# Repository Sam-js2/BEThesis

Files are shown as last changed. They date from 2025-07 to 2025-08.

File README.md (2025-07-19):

# Supporting Material for Thesis C
**S Shelton z5359712**

This repository contains supporting material for Thesis C, including code, schematics and Altium design files.

A video of the device operating can be found [on YouTube here](https://youtu.be/sB7mTB_tMe0) [https://youtu.be/sB7mTB_tMe0].

The poster that was presented at SOFE2025 is here, as well as my Thesis C slides and an uncompressed copy of the thesis manuscript.

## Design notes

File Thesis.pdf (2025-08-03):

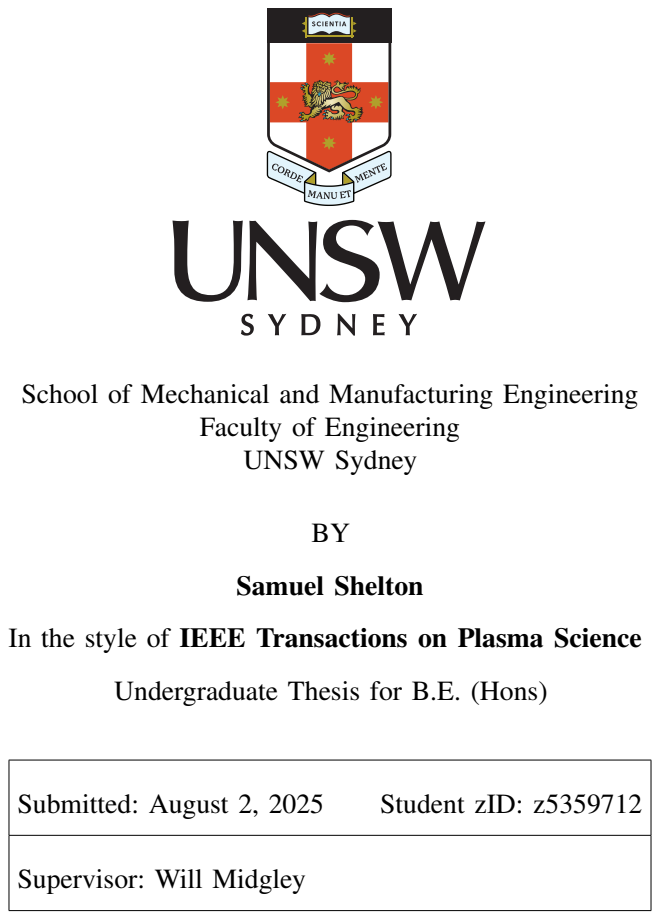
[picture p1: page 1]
BY Samuel Shelton; Submitted: August 2, 2025; Student zID: z5359712

School of Mechanical and Manufacturing Engineering

Faculty of Engineering
UNSW Sydney

In the style of IEEE Transactions on Plasma Science

Undergraduate Thesis for B.E. (Hons)

Supervisor: Will Midgley

MANUSCRIPT BACKGROUND

The work in this thesis was presented as a poster at the Symposium on Fusion Engineering, held 23–26 June 2025 on the MIT Campus in Cambridge, MA. This thesis is an extended version of a six-page conference paper that is being submitted to the IEEE Transactions on Plasma Science journal for the SOFE 2025 special issue. The formatting of this thesis is extremely close to the IEEE requirements (including the required biographies and Americanized spelling), but with some basic changes like the inclusion of an appendix (to house what would otherwise live on the journal’s website as supporting material) and the removal of references to submission and publication dates. Also please note that these pages are significantly denser than the 20 page (single column) limit, so the length of the paper is proportionally shorter.

ORIGINALITY STATEMENT

‘I hereby declare that this submission is my own work and to the best of my knowledge it contains no materials previously published or written by another person, or substantial proportions of material which have been accepted for the award of any other degree or diploma at UNSW or any other educational institution, except where due acknowledgement is made in the thesis. Any contribution made to the research by others, with whom I have worked at UNSW or elsewhere, is explicitly acknowledged in the thesis. I also declare that the intellectual content of this thesis is the product of my own work, except to the extent that assistance from others in the project’s design and conception or in style, presentation and linguistic expression is acknowledged.’

Signed:

Date:

# 2D Hall Arrays for High Resolution Tokamak Magnetic Field Imaging

Samuel Shelton and Will Midgley

Abstract—This paper presents the use of a two-dimensional array of magnetic field sensors designed to image the magnetic field produced in the vacuum vessel of the upcoming SOUTH tokamak. Designed to de-risk engineering efforts by allowing for precise mapping of toroidal and null field configurations within the plasma boundary region, this represents the first use of such a device within the context of fusion. Using low-noise circuitry and multiple analogue-to-digital converters in parallel, the device can achieve up to 20 kHz of analogue bandwidth across 256 sensors, with an effective sensitivity of 0.32 mT against a dynamic range exceeding ±150 mT. The device can also be operated in a real-time mode using a micro-controller, allowing interactive visualizations of magnetic fields for outreach and pedagogical purposes. Preliminary imagery and simulated reconstructions are presented, with the device intended to assist with the research and development, manufacturing and commissioning of the SOUTH tokamak in anticipation of a first pulse in late 2026.
Index Terms—tokamak, diagnostics, instrumentation, magnetovision, Hall effect, magnetic field mapping
I. INTRODUCTION
T HE SOUTH tokamak (shown in Fig. 1) is being developed at the University of New South Wales in Sydney, Australia as a student project called AtomCraft [1]. SOUTH—the Student Operated Undergraduate Tokamak with Hydrogen—will be the first tokamak designed and built entirely by undergraduates. It will be a compact, spherical tokamak employing conventional magnets and utilizing a combination of ohmic heating and electron cyclotron resonance heating (ECRH). The design is influenced primarily by the Danish NOTH tokamak [2] and its predecessor, Tokamak Energy’s ST-25 [3], with the coil and power supply designs inspired by the University of Seville’s SMART [4].
SOUTH is expected to operate with a toroidal on-axis magnetic field of 100 mT and an approximate 100 ms pulse, although these specifications are targets and are subject to change. The device has a major radius of approximately 0.3 m, with a vacuum vessel diameter of 30 cm. Initial plasma operations are expected to begin in late 2026, with plasma currents of 3 kA and plasma temperatures of about 10 eV expected [1]. AtomCraft’s primary focus is pedagogical, with the initiative focused on providing students with hands-on experience in fusion engineering from as early as their second undergraduate year. SOUTH is AtomCraft’s first project, with more nuclear-related projects and upgrades planned for the future.
S. Shelton and W. Midgley are with the School of Mechanical and Manufacturing Engineering, UNSW Sydney, and the SOUTH collaboration. Corresponding author W. Midgley, w.midgley@unsw.edu.au.
Supporting materials for this paper are available at https://github.com/Sam-js2/BEThesis (https://github.com/Sam-js2/BEThesis) and https://youtu.be/sB7mTB tMe0 (https://youtu.be/sB7mTB_tMe0)

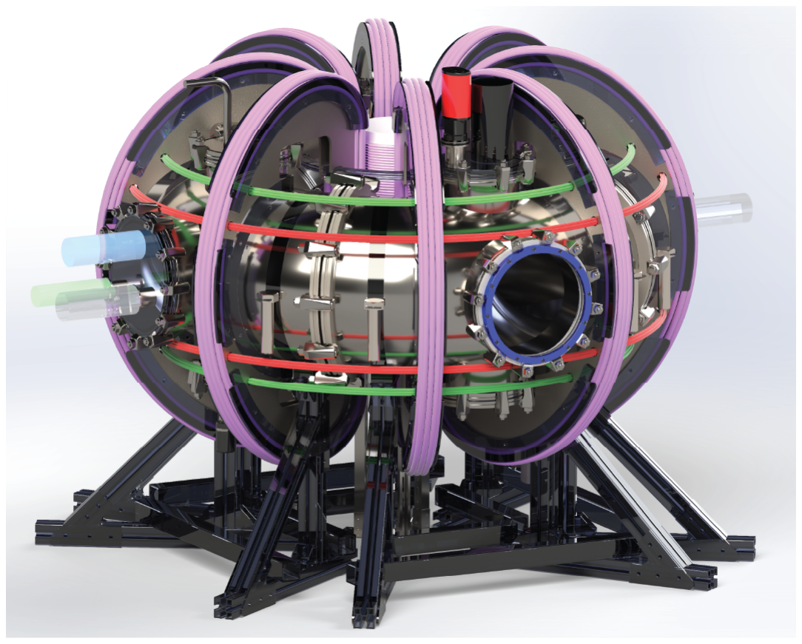
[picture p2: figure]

Fig. 1. A render of the upcoming SOUTH tokamak, with placeholder instrumentation, vacuum, fueling and RF equipment, with the ‘Princeton Dee‘ toroidal field (TF) coils are in purple and the poloidal field (PF) coils in red and green [1].

As a student project, AtomCraft operates under strict budgetary constraints and with a strong operational emphasis on safety and risk management. A significant portion of funding is sourced externally from philanthropic institutions and commercial fusion organizations, necessitating clear and communicable results for outreach purposes. The idea of a two-dimensional Hall array emerged as a tool to detect technical issues with the magnet system (particularly the critical toroidal field, produce by the ‘Princeton Dee’ magnets with a configuration as shown in Fig. 2) prior to plasma operation, with potential as an outreach and recruitment tool due to its visual and interactive nature.

A. Hall sensors and magnetic sensor arrays in Fusion
Hall effect sensors are widely used in fusion engineering for magnetic field monitoring [5], plasma diagnostics [6], and current sensing [7]. Low-density arrays have an established use in magnetic field mapping [8], and a high-density onedimensional array of Hall sensors has been demonstrated as an effective tool for measuring both vacuum and plasma-generated poloidal magnetic fields in magnetically confined steady-state plasmas [9].
1) ITER Magnetic Diagnostics: Chavan et al.’s 2009 paper in Fusion Engineering and Design serves as a summary of all the magnetic field diagnostics intended for use at ITER, while

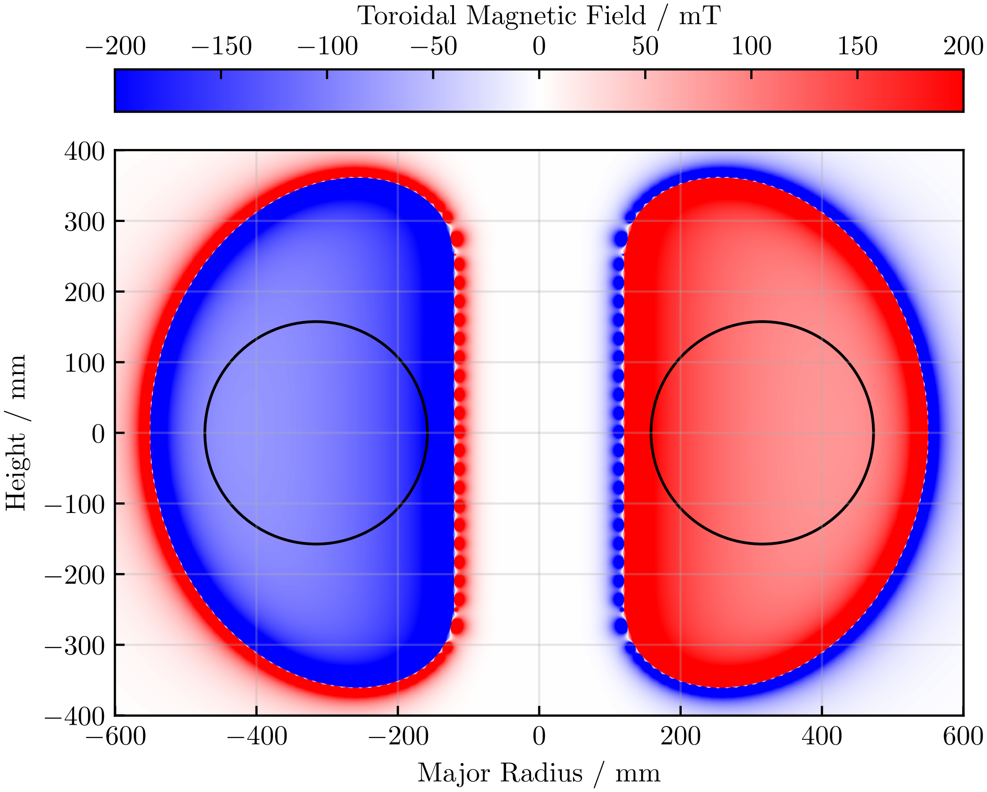
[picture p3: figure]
Major Radius / mm; Height / mm; Toroidal Magnetic Field / mT

Fig. 2. Toroidal magnetic field generated by SOUTH during a 3 kA plasma pulse. The field here is clipped to ±200 mT and was computed using the Biot-Savart law on a discretized model of the ‘Princeton Dee’ TF coils [1].

also discussing risks to the project [6]. The diagnostics set of ITER is to consist of 120 Hall probes for tangential field monitoring, 54 for radial field monitoring and 12 for toroidal field monitoring. This data is to be used to inform closed-loop control algorithms, and in post-pulse plasma reconstruction. These Hall probes are heavily redundant to account for any probe failures due to excess exposure to radiation [6]. Chavan et al. further identify the ITER-specific design drivers that informed the selection of this diagnostics setup. They include the ability to work over ITER’s long plasma pulse lengths, in the presence of high levels of neutron radiation, steep requirements for accuracy, precision and system availability, resistance to various kinds of electrical interference, and several requirements regarding data acquisition [6].
In a related follow-up paper, Duran ˇ et al. detail the design of a custom semiconductor Hall Effect sensor for use at ITER [11]. To address the challenges previously identified by Chavan et al. [6], Duran ˇ et al. use a metallic bismuth process and large sensor area to achieve sufficient radiation hardness. Their custom sensor, shown in Fig. 3a, is able to operate with sufficient sensitivities across a large range of magnetic field strengths up to ±6 T, with radiation hardness well in excess of anything commercially available. Fortunately, neutron irradiation and extended pulse lengths are not anticipated at SOUTH, and there is no closed loop control planned for the initial operating configuration. While ITER’s diagnostics are cutting edge, they are not as applicable to UNSW’s much smaller tokamak as might initially be expected.
2) Magnetic Field Diagnostics in Spherical Tokamaks: Other, spherical Tokamaks are more comparable to SOUTH geometrically. The QUEST Tokamak, a mid-sized spherical Tokamak located in Japan, uses an advanced closed-loop control system to achieve extremely stable plasma pulses lasting up to six hours [12]. A key part of this control system is a complex arrangement of Hall effect sensors (both single and tri-axial) located at key points on the outside of the vacuum vessel, as

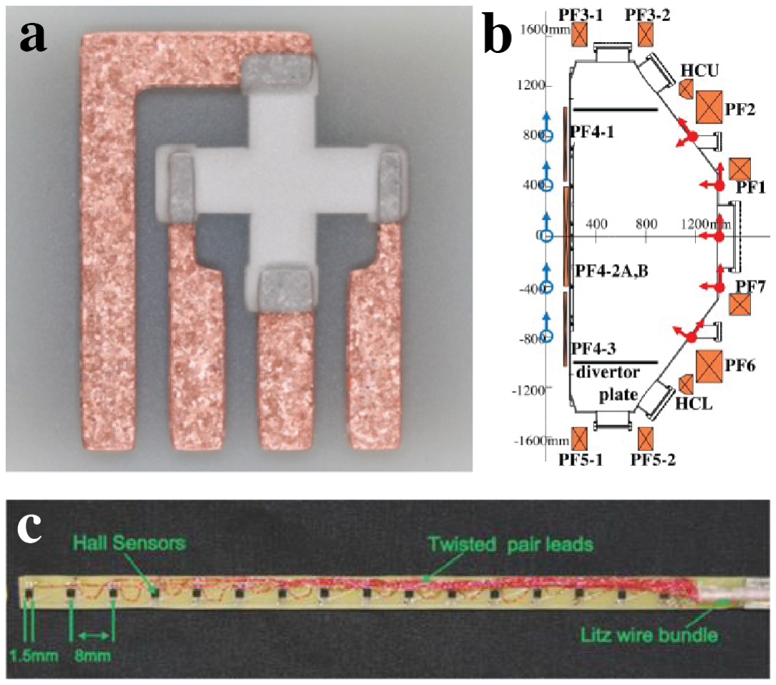
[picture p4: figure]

Fig. 3. Fusion applications of Hall sensors: a) Custom Lead-Bismuth Hall sensors for ITER [10]; b) Hall sensor placement for QUEST [5]; c) Insertable Hall array for poloidal field monitoring [9].

shown in Fig. 3b. These sensors provide output data which is integrated at 100 kHz, and fed into a control loop running at 4 kHz [5]. The sensors themselves are accurate over a range of ±1600 G (160 mT), which is comparable with the peak field expected on SOUTH. The Hall sensors here are particularly useful for combating the drift accumulated by the analog integration of Rogowski coil signals over long plasma pulses [5].
The small CASTOR tokamak featured a small array of eight commercial Hall effect sensor ICs integrated into the stainless steel vacuum vessel [10]. Duran ˇ et al.—the same Duran from ITER [11]—integrated sensors, power and signal ˇ conditioning circuitry onto a single small PCB, and put the entire device inside the Tokamak vacuum vessel—the first ‘invessel environment’ use of such sensors. The results prove the efficacy of commercial Hall effect sensors in environments with relatively low (compared to ITER) amounts of radiation and ambient temperatures up to 150 →C [10]. These results are very relevant to the SOUTH tokamak, which is expected to have conditions (in terms of radiation and ambient temperatures) similar to CASTOR. While Duran ˇ et al.’s work is not directly applicable to SOUTH because it is designed as a plasma diagnostic, the success of the project proves the viability of using commercial sensors for fusion applications.
3) Insertable Linear Array Probe: Stevenson et al.’s 2014 paper presents a linear array of 16 Hall effect sensors with a spacing of 8 mm, designed and fabricated on a printed circuit board [9]. This linear array (essentially a long, thin stick, as shown in Fig. 3c) is then inserted into the plasma through a hole in the vacuum vessel, and rotated around its axis of insertion to capture a full range of data. This implementation is extremely innovative and the most comparable existing design to what is proposed in this paper, and the use of twisted pairs, differential amplifiers and analogue anti-aliasing filters distinguish it as

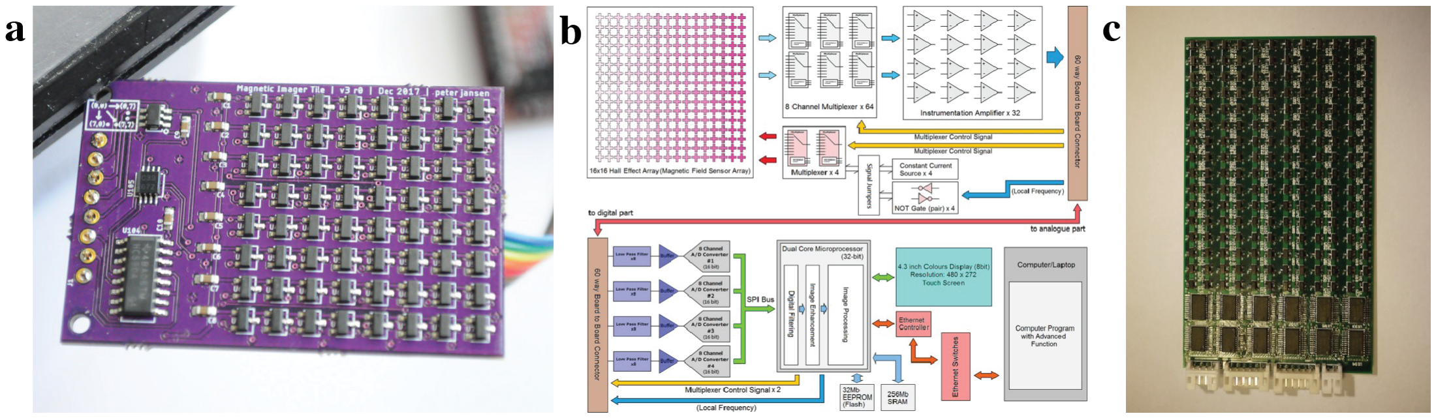
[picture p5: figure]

Fig. 4. Non-fusion applications of Hall arrays: a) Jansen’s Tile V3 [13]; b) Block diagram of Liang’s implementation [17]; c) Gaussense PCB [14].

the most complete implementation thus far.

B. Hall Arrays Outside of Fusion
Two-dimensional Hall arrays have been used outside of fusion as educational tools [13], in consumer electronics [14], and for non-destructive testing [17] and metallic object detection [18]. These devices all share a basic systems architecture underpinned by the use of multiplexed sensors, but implementations vary widely in terms of the data acquisition architecture and varying levels of analog filtering and complexity.
1) The Works of Peter Jansen: Peter Jansen’s work on these sensors on Hackaday served as a strong initial inspiration for this project. Jansen’s first Hall board was a 12 → 12 array that featured closely packed Hall Effect ICs fed into an analog-todigital converter (ADC) through cascaded I2C multiplexers. This implementation was slow—only achieving 10–30 samples per second (SPS) operation depending on the microcontroller used—mostly due to the speed of the I2C bus [15]. His next iteration, version 3.0 (shown in Fig. 4a), used a smaller 8 → 8 array and a binary counter connected to a clock to operate the multiplexers, enabling higher sampling rates up to 2,000 SPS [13].
While a great improvement, Janesen notes that the implementation is still bottlenecked by the slow ADC [13], and future devices could get around this by using a more powerful microcontroller. All of Jansen’s tiles suffer from a notable lack of any form of buffering or filtering, leaving the digitized signal to be susceptible to aliasing and rendering the entire setup vulnerable to electromagnetic interference. The PCB is also designed without a ground plane, among other issues that make the design susceptible to both the creation and absorption of EMI, necessitating a complete analog overhaul if the device were ever to be applied to fusion.
2) Real-time Magnetovision Camera: Liang et al.’s 2017 paper details a well designed and tightly integrated magnetovision imaging device [17]. Their device features a 16→16 array of custom Hall effect sensors whose outputs are multiplexed, buffered and sampled with an ADC—four in parallel for the 16 → 16 array—commanded by a microcontroller, which also coordinates the operation of the custom Hall effect sensors, as shown in Fig. 3b. Liang et al. apply best practice analog design using anit-aliasing filters and buffers, and completely separate the digital and analog PCBs to provide a level of modularity that makes manufacturing and testing easier, while also allowing for the digital components to be readily swapped out.
Liang et al. ran their SPI busses at 21 MHz and stored the excessive amount of data generated in discrete external memory, before sending it to a PC for analysis over ethernet [17]. Although designed to operate in ‘real-time,’ Liang et al. still achieve an impressive 600 SPS, more than enough for their specific use case but not enough for imaging the fast changing fields on SOUTH. This real-time application is also why a bilinear approach is used over the preferable but much more computationally intensive bicubic method for spatial interpolation. The design itself is also much to bulky to fit inside SOUTH’s vacuum vessel, but the innovative use of separate modular analog and digital PCBs could provide a path to compact and performant implementation.
3) Hall Arrays for User Interface Design: Liang et al.¹ proposed the use of an array of commercial Hall effect sensors as a way to sense the orientation of a writing stylus for a digital tablet display in their 2012 paper [14]. This Guassense technology was designed to enable devices to distinguish between stylus and finger inputs, sense the tilt and angle of a stylus, and detect a stylus hovering over the surface of a screen. Guassense was designed to augment existing devices, being placed behind LCD screens to add a new layer of user interactivity.
The hardware implementation, shown in Fig. 4c, contained 192 commercial Hall sensors multiplexed into a microcontroller’s inbuilt ADC. Bicubic interpolation was used to enhance the spatial resolution of images, and the polling rate was “consistently above 60 fps” [14]. Guassense suffers from most the same issues as Jansen’s implementations, and could benefit greatly from the incorporation of a proper buffering and filtering regime. It is worth commending the vision of Guassense: since its publication in 2012, Apple has gone on to successfully commercialize many of the unique goals of the project, namely the detection of stylus angle, tilt and hover [16]. While Apple doesn’t use an array of Hall effect sensors, Liang et al. successfully anticipated a market demand that

1A different Liang et al.. from [17].

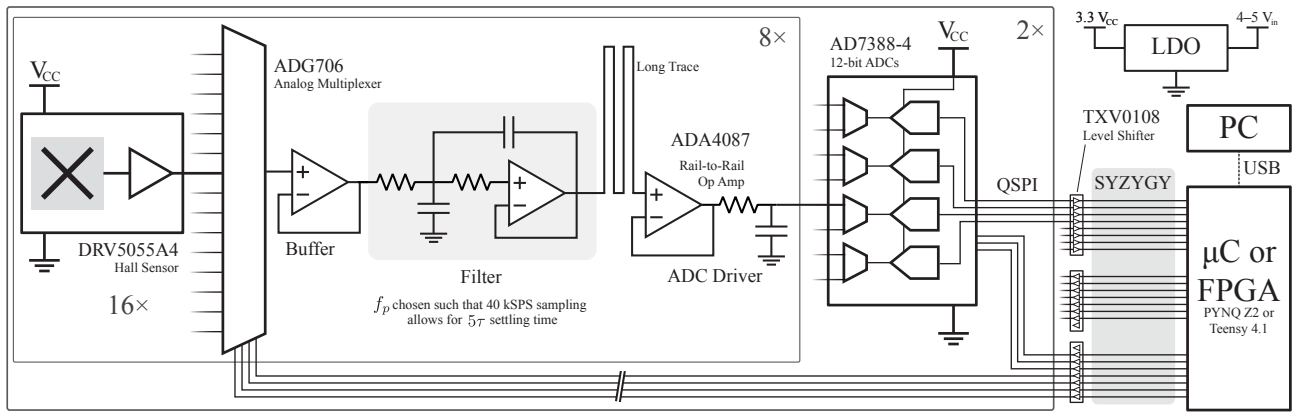
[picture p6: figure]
μC or FPGA; PYNQ Z2 or Teensy 4.1; DRV5055A4 Hall Sensor; VCC; ADG706 Analog Multiplexer; ADA4087; Buffer; Filter; ADC Driver; AD7388-4 12-bit ADCs; QSPI; SYZYGY; TXV0108 Level Shifter; chosen such that 40 kSPS sampling; allows for; settling time; LDO; Rail-to-Rail; USB; Op Amp; Long Trace; 3.3 VCC; 4–5 Vin

Fig. 5. Simplified circuit schematic showing the operation of the device.

would be only be realized more than a decade later.
4) Unpackaged Scanned Array: Cai et al.’s 2024 paper presents an array of 256 unpackaged (not contained in black plastic packages) Hall effect sensors that moved around on an X–Y drive to image a large area at an extremely high resolution [18]. Cai et al. are primarily concerned with spatial fidelity, so the use of unpackaged sensors allow the ‘pixels’ to be placed extremely close together, and the X–Y drive allows them to combine adjacent images to enhance both resolution and frame size. Cai et al. use external data acquisition boards, power supplies and control systems, so while the sensor itself is compact, the system still has a large overall footprint. While Cai et al.’s work is likely the least applicable to fusion applications of the devices discussed due to its extremely slow sampling rate, the use of unpackaged sensors has potential for future, more advanced devices.
C. Tokamak-specific Requirements for Hall Sensors
Based on existing implementations of Hall arrays both inside and outside of fusion and identified design constraints, the following were identified as the key properties required of a Hall array for use in magnetic field imaging on the SOUTH tokamak:
Sensitivity and Range: The array must measure both the strong toroidal field at approximately 100 mT and potential near-zero stray radial magnetic field components; an effective sensitivity of ↑ 1 mT is highly desirable.
Bandwidth and Sampling: Given the short pulse duration of 100 ms, the array requires a high analog bandwidth and associated sampling rate. A bandwidth exceeding 10 kHz— the PWM switching speed of SOUTH’s power supplies—is desirable.
Miniaturization: The array must fit within the vacuum vessels and through its standard flanges with a maximum width of 150 mm, while still covering the plasma boundary region of interest.
Environmental: The array must maintain a low noise floor (in order to achieve the desired sensitivity) and resist environmental sources of electromagnetic interference (EMI), including switching transients and RF interference, particularly around the industrial, scientific and medical (ISM) band at 13.56 MHz.
Existing magnetic field diagnostics in Tokamaks exist largely in service of physics applications, rather than in verifying the engineering itself and the ability to construct the magnetic field conditions intended. This is largely due to the much higher degree of engineering confidence in large scale projects like ITER, especially when compared to undergraduate work at UNSW. What diagnostics do exist are largely external to the vacuum vessel itself and are predominantly coil based, sacrificing almost all spatial resolution for temporal resolution and bandwidth.

II. METHODOLOGY &DEVICE DESCRIPTION
The final device works by simultaneously sampling eight sensors using two discrete ADCs, with 16:1 multiplexing into each filter and additional 2:1 multiplexing in-package on the ADC ICs; the device operating methodology summarised in Fig.
5. The analog and digital electronics are physically separated, allowing the analog sensor board to fit inside the vacuum vessel while the digital control board is located externally. This modular design also supports multiple digital processing configurations, customized for specific use cases. A 1/16th scale prototype was constructed to de-risk the final design, which was manufactured and assembled by a PCB assemblyhouse in China that used a combination of standard and specialized imported components.
A. Analog Electronics
The selected Hall sensor is the Texas Instruments DRV5055A4, which supports a measurement range up to ±179 mT when powered at 3.3 V and offers an analog bandwidth of 20 kHz [19]. Each sensor outputs a voltage proportional to the magnetic field (V ↓ B), with zero field corresponding to VCC/2. This architecture enables all 256 sensors to share a common reference with both ADCs, ensures that all voltages remain within the linear region of all operational op-amps, and provides some common-mode immunity from EMI.

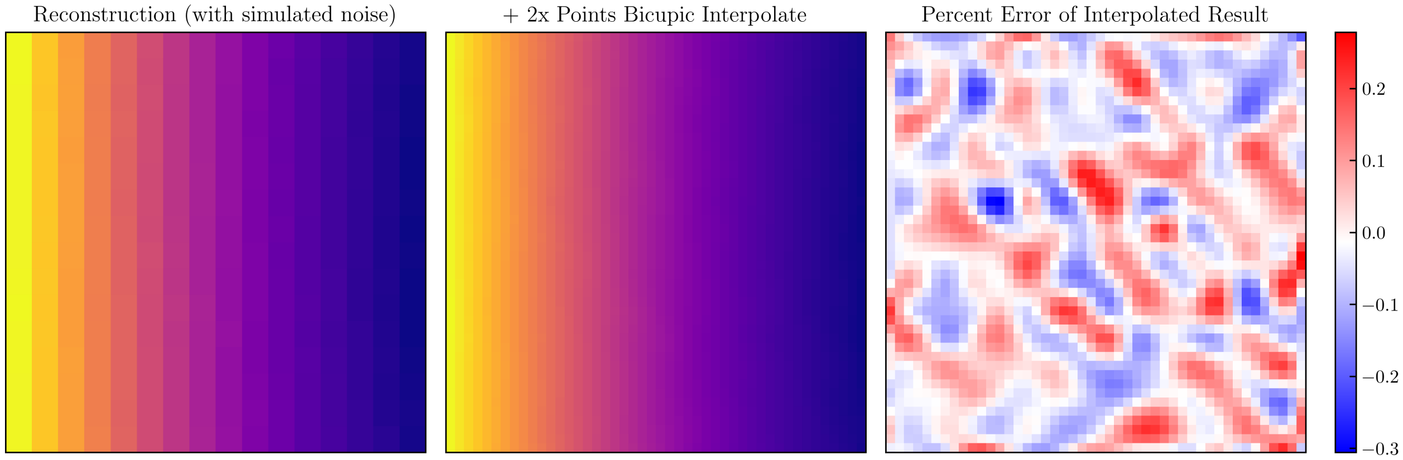
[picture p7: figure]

Fig. 6. Effects of bicubic interpolation, and error of interpolated result of reconstructed images, sharing a reconstruction model with Fig. 9.

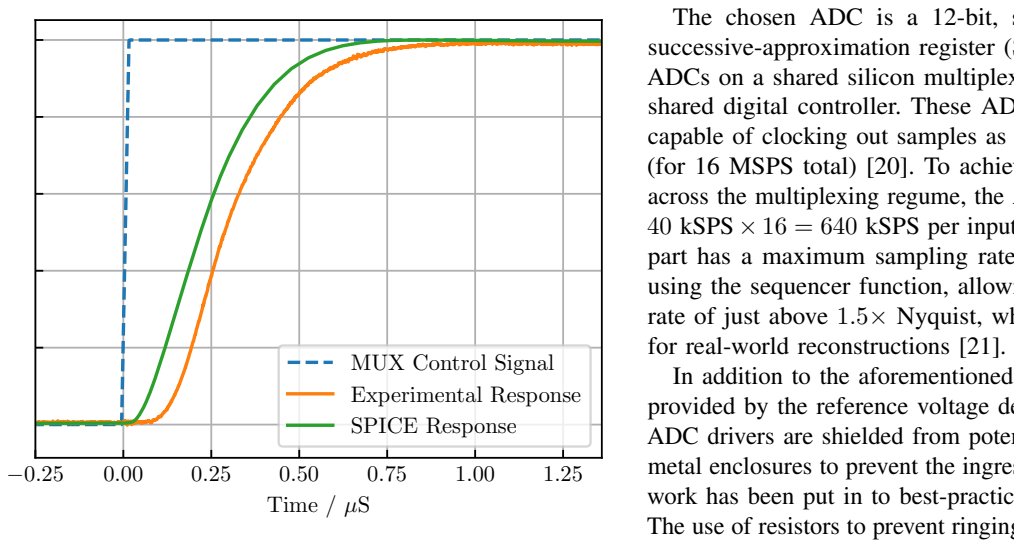
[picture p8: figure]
Time / µS; MUX Control Signal Experimental Response SPICE Response; for real-world reconstructions [21].

Fig. 7. Normalized experimental and simulated (with LTspice) filter settling behavior. The LTspice model is also shown in Fig. 11, and the experimental data was captured simultaneously with that of Fig. 15.

Sensor outputs are routed through high-performance analog multiplexers, buffered by low-noise rail-to-rail op-amps, and fed through single-stage Sallen-Key low-pass filters, before being buffered again by an ADC driver and digitized. The filter schematic is shown in Fig. 11, with an LTspice simulation of the filter response compared with the experimental settling shown in Fig. 7. The filter’s pole frequency, fp ↔ 1.2 MHz, is tuned to allow five time constants of settling at a sampling rate of 40 kSPS, after accounting for the increased sampling rate required for multiplexing. This filter mitigates high-frequency switching noise and RF interference but does not serve as an anti-aliasing filter. Consequently, the system is susceptible to aliasing from interference in the 20–1,000 kHz range, but most sources of external noise (including the ISM band) should be sufficiently suppressed. The inability to implement effective anti-aliasing without incurring significant cost is the primary limitation of the multiplexed topology.

The chosen ADC is a 12-bit, simultaneously sampling, successive-approximation register (SAR) part, featuring four ADCs on a shared silicon multiplexed to eight inputs with a shared digital controller. These ADCs share a quad-SPI bus capable of clocking out samples as fast as 4 MSPS per ADC (for 16 MSPS total) [20]. To achieve the Nyquist frequency across the multiplexing regume, the ADC must sample at least 40 kSPS → 16 = 640 kSPS per input channel, and the selected part has a maximum sampling rate of 1 MSPS per channel using the sequencer function, allowing a maximum sampling rate of just above 1.5→ Nyquist, which should be acceptable

In addition to the aforementioned common-mode immunity provided by the reference voltage design, both the ADCs and ADC drivers are shielded from potential interference inside µmetal enclosures to prevent the ingress of noise, and significant work has been put in to best-practice PCB design approaches. The use of resistors to prevent ringing, multiple stitched ground planes, digital and analog traces intersecting across layers at 90→ and a liberal deployment of LC filters in the power supply circuitry all contribute to reducing the generation and ingress of EMI.

B. Digital Electronics
The compact dimensions inside SOUTH’s vacuum vessel necessitate a separate digital control assembly. The main analog PCB includes three buffer/level shifter ICs which enable operation with both 3.3 V and 1.6 V logic, allowing interfacing with a wide range of controllers over a standard, high-performance SYZYGY FPGA connector. So far two compatible digital interfaces have been designed: one for userfriendly, interactive operation using a microcontroller, and another for high-performance data acquisition using an FPGA. The microcontroller-based solution uses a Teensy 4.1 [22] and is designed for sampling at up to 6 kSPS using dual hardware SPI interfaces. The Teensy can support 24 MHz onewire SPI, but can achieve 48 MHz with reduced stability. In this configuration, the ADC’s built-in hardware oversampling can be used to reduce bandwidth and mitigate aliasing, while also decreasing the amount of data produced. Full-rate sampling is not feasible due to bus speed and memory limitations.
To ensure data can be communicated correctly between the microcontroller and PC analysis software, a proprietary datapacket has been developed, with a layout as shown in Tab. I. This packet includes many synchronous bits at the start and end of the binary data, to make separating packets easier with inbluilt python and MATLAB functions like serial.readuntil. The packet includes empty space (the packet size padded to 512 bytes) and a version number to allow future expansion, and includes a packet counter and space reserved for CRC checksums to prevent both packet loss and data corruption. An example of the microcontroller digital logic operation is shown in Fig. 15 in the results section, and a representative sample of the microcontroller code is contained in Lst. 1 in the Appendix.

TABLE I
STRUCTURE OF SERIAL PACKETS
Field Name | Type | Bytes Description
sync1 | uint8_t | 1 | Sync byte 1 (0xAA)
sync2 | uint8_t | 1 | Sync byte 2 (0xBB)
sync3 | uint8_t | 1 | Sync byte 3 (0xCC)
sync4 | uint8_t | 1 | Sync byte 4 (0xDD)
count | uint32_t | 4 | Packet counter
timeStamp | uint32_t | 4 | Optional timestamp
dataSize | uint16_t | 2 | Number of uint16_ts
version | uint8_t | 1 | Packet version (0x01)
flags | uint8_t | 1 | Reserved/unused flags
data | uint16_t[192] | 384 | Data payload
spareData | uint8_t[104] | 104 | Reserved
CRC | uint32_t | 4 | Space for Checksum
sync5 | uint8_t | 1 | Sync byte 5 (0xEE)
sync6 | uint8_t | 1 | Sync byte 6 (0xFF)
sync7 | uint8_t | 1 | Sync byte 7 (0x11)
sync8 | uint8_t | 1 | Sync byte 8 (0x22)
Total | | 512 | Total packet size in bytes

The FPGA implementation uses a Pynq Z2 FPGA development board, capable of exceeding the 40 kSPS Nyquist frequency required for the 20 kHz sensor bandwidth. This is achieved using two four-wire SPI interfaces in parallel at bus speeds exceeding 50 MHz. The FPGA configuration is intended for high-performance, triggered measurements, though real-time interaction has been demonstrated as possible by other groups [17] and could be developed in the future.

C. Power Supply
Due to the analog electronics’ reliance on the power rail for both a supply and reference voltages, a low-noise linear dropout regulator (LDO) is used to provide a stable and clean 3.3 V common carrier voltage from an input voltage in the range of 4–5 V. PSice simulations of this power supply, shown in Fig. 8, show acceptable startup behavior that meets the requirements set by the ADC [20], [23]. MOLEX micro-fit cables were chosen because of their extremely small PCB footprint, robust supply chain and adjacency with the mini-fit JR line of products already in use by SOUTH, with crimping tools already available in various accessible research labs. Ideally the device should

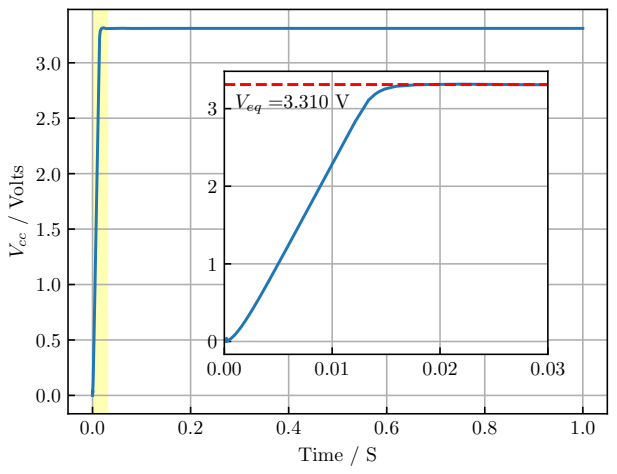
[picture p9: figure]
Time / S; Vcc / Volts; Veq =3.310

Fig. 8. PScipe simulation of power supply output voltage, with detail showing startup time. In steady-state operation noise is expected to be 4.4 µVRMS [23].

receive its 4–5 V input voltage from an external linear power supply, but low-noise operation (as low as 4.4 µVRMS [23]) is still achievable when powered from a quality switching mode converter. The LDO is connected to several ground planes to ensure adequate cooling, but running on closer to 4 Vin is advisable to prevent excessive heat dissipation.

D. Data Processing & Analysis
To convert the raw ADC output codes into meaningful images, each code is mapped to a spatial location in two dimensions, then converted to a voltage and a magnetic field using the sensor sensitivity and DC offset. This processing is performed externally on a host computer. For the FPGAbased implementation, additional processing is required to apply a phase correction to each sensor’s fully reconstructed (with sin x/x interpolation) analog waveforms to correct for rolling-shutter effects that are an inevitable consequence of the multiplexed topology. For real-time operations, the acquisition rate is significantly faster than the display refresh rate, rendering rolling shutter effects negligible.
Bicubic interpolation between adjacent sensors has been employed in previous Hall array implementations [14], [17], and is used here in post-processing where the computational cost is negligible. Fig. 14 presents selected results enhanced via bicubic interpolation; this method is effective when the spatial resolution of the sensor array exceeds the granularity of the magnetic field being reconstructed, such as in the case of the tokamak’s toroidal field cross-section, but localized field—such as those generated by small button magnets—are vulnerable to artifacting.
E. Intended Use in SOUTH Tokamak
The primary application of the device in the SOUTH tokamak is to validate the magnitude and spatial configuration of the toroidal field, which should ideally look like the field shown in Fig. 2. Fig. 9 illustrates a numerically simulated

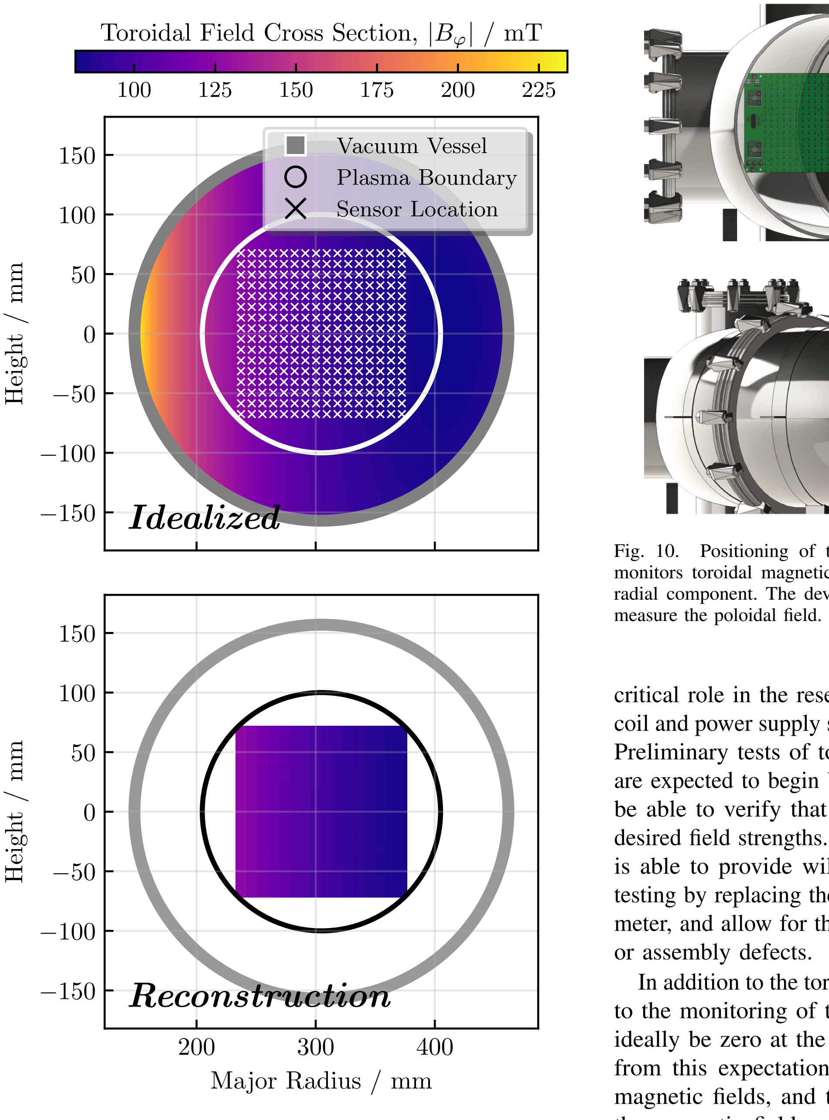
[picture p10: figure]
Toroidal Field Cross Section, |B'| / mT; Height / mm; Idealized; Vacuum Vessel Plasma Boundary Sensor Location; Major Radius / mm; Reconstruction; measure the poloidal field.; or assembly defects.

Fig. 9. Idealized plot shows sensor geometry (a 9 mm pitch) within SOUTH and an ideal field simulation during the ‘flat top‘ of a 3 kA pulse, shared with Fig. 2; the reconstructed field accounts for sensor geometry and noise.

toroidal field for a 3 kA plasma in SOUTH, alongside a simulated reconstruction incorporating modeled device noise. The imaging capability of the array is expected to confirm the characteristic Bω ↗ 1/R relationship and allow comparison with multiphysics simulations. The device could also potentially offer some quantitative measurement of magnetic field ripple; a device bandwidth of 20 kHz will be able to get some basic measurements of the ripple in the 10 kHz switching frequency device, but because that 10 kHz signal is a square wave a full reconstruction would not be possible (and would require a sampling rate of at least 30–50 kSPS by rule of thumb [21]). While applying this device to the full assembled tokamak system (in the configuration shown in the upper segment of Fig. 10) is the primary design goal, the device will also serve a

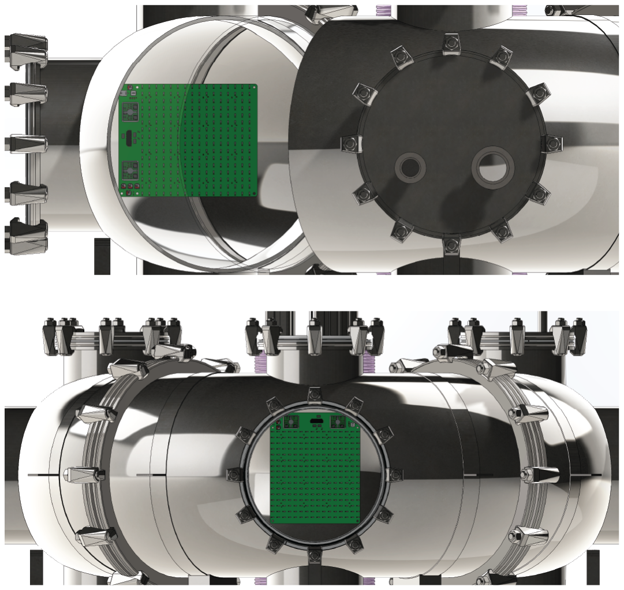
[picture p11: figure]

Fig. 10. Positioning of the tile within SOUTH. The top configuration monitors toroidal magnetic field while the bottom configuration monitors radial component. The device could also be positioned facing upwards to

critical role in the research and development of the individual coil and power supply systems before the full design integration. Preliminary tests of toroidal field coils at fractional currents are expected to begin by the end of 2025, and this device will be able to verify that the applied currents are achieving the desired field strengths. The instant feedback that the Hall array is able to provide will be able to improve the efficiency of testing by replacing the use of a single, lower-bandwidth gauss meter, and allow for the timely detection of any manufacturing

In addition to the toroidal field, the device can also be applied to the monitoring of the radial magnetic field, which should ideally be zero at the center of the toroidal field. Deviations from this expectation would indicate the presence of stray magnetic fields, and this would in turn indicate issues with the magnetic field system that could be flagged for further investigation. Since each sensor measures the field component parallel to its normal vector, the array must be positioned to intersect the field lines of interest, as shown in the bottom section of Fig. 10. A poloidal application, similar to [9], is also possible, but this would be particularly intolerant of sensor misalignment and require a high sensitivity.

F. Initial 1/16 Scale Prototype
Because of the significant cost investment of the final device (each sensor cost about A$1 and each ADC about A$ 80, with a minimum order quantity of two devices) a 1/16th scale prototype was designed to test the PCB manufacturing quality and analog electronics. The prototype, shown in Fig. 11, featured a two-stage analog filter that was unstable in its manufactured state. After making some modifications to the filter and reducing it to a single stage, the filter achieved the performance shown in Fig. 11.

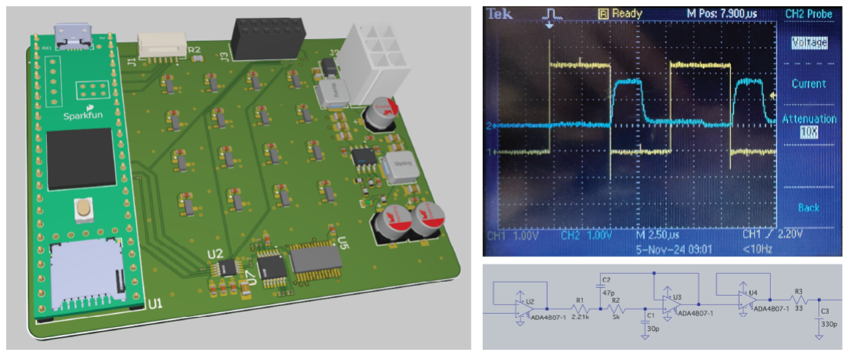
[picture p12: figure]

Fig. 11. 1/16th Scale Prototype, with experimental filter testing results and filter schematic shown.

The prototype used 0201 size components, initially chosen so that a full two-stage filter setup could be fit inside a surface-mount EMI shield, but the difficulty in modifying the components (because they were so small) combined with the dropping the second filtering stage informed a switch to much more accessible 0603 components for the final design. This decision was also influenced by the significant cost penalty that 0201 assembly incurred, and the increased parts availability (i.e., a wider range of resistances and capacitances to use a more favorable filter configuration) and flexibility provided by 0603 parts that could be soldered by hand to accommodate changes to the filters or drivers after initial manufacturing. Another key objective of the prototype was testing the manufacturing tolerances of the ‘via-in-pad’ technology, which dramatically reduces routing complexity by embedding vias directly into the very fine pitch (< 0.65 mm) pads of the multiplexers and op-amps. No short circuits between adjacent pads were identified by the manufacturer, and none were found during manual inspection. The prototype also functioned as a test-bed for the development of PC-based analysis software while the final device was still having its design finalized, parts sourced and circuit boards printed, dramatically accelerating the project’s software development timeline.

III. RESULTS
The final device (shown in Fig. 12) was delivered with no debilitating design of manufacturing defects, and testing to-date is indicative of a comprehensive fulfillment of the design goals outlined in the introduction. The micocontroller digital control board is capable of much faster sampling than anticipated, with sampling up to 10 kSPS possible. This makes further development of the FPGA implementation unnecessary until the full 40 kSPS sampling is required for full-bandwidth testing of SOUTH’s coils, anticipated for mid–late 2026. Interactive plotting in real-time also works reliably, although software Python and MATLAB-based serial frontends limit the data collection rate to about 250 SPS, meaning 10 kSPS sampling can only be achieved over short periods of time when taking a ‘triggered’ measurement. This means that an FPGA development board—with external, discrete and plentiful DRAM—is necessary for extended operation at high sampling rates.
Some preliminary static imagery (averaged over many acquisitions) is shown in Fig. 14, but the device’s functionality and dynamic imaging capabilities are best demonstrated more

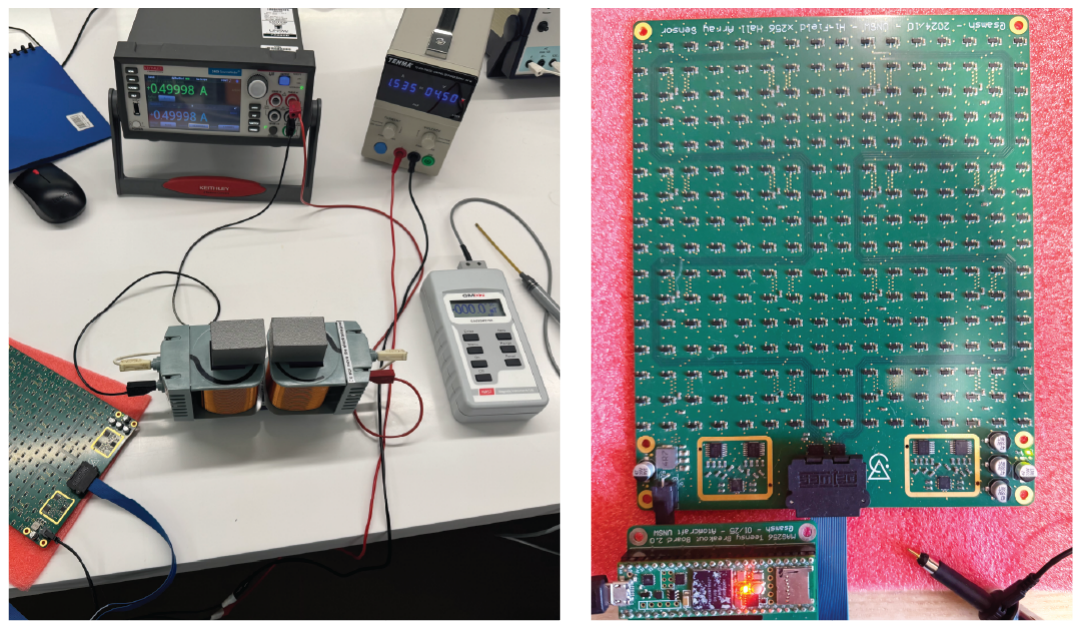
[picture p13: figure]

Fig. 12. Linearity calibration setup with source meter, gauss meter, and ferrite core electromagnet (left), and close-up of the completed device (right) with the Teensy digital controller board partially shown.

interactively as in the video contained within the supporting material or hosted on YouTube, here. This video should be considered essential viewing.

A. Quantification of Noise
The noise of all individual sensors were measured with no applied magnetic field over a sampling period of 10,000 samples, collected with a generous settling time to maximize the effectiveness of the analog electronics. As shown in Fig. 13, all 256 sensors perform similarly and there is no significant geometric correlation of noise statistics between adjacent sensors or sensors that share filters or ADCs. The device demonstrates a very low AC RMS noise floor below one leastsignificant bit or about 0.086 mT, with a corresponding effective sensitivity of 0.32 mT. The noise statistics do not drop off as expected with the introduction of hardware oversampling, likely because the noise floor is dominated by quantization noise. This indicates that future iterations could benefit from the use of higher-resolution ADCs, although the utility of such an improvement is questionable.
This is an exceptionally low noise floor, well in excess of the requirements identified as part of the projects literature review. This noise floor is low enough that it likely enables new uses of the device, specifically in the monitoring of SOUTH’s (much smaller) poloidal fields. The high dynamic range of the instrument, combined with its sensitivity, would allow for the monitoring of small amounts of ripple ontop of large DC magnetic fields.
B. Calibration
The DC offset at zero magnetic field was calculated using the same dataset as the noise measurements. Sensor calibration was performed with a ferrite-core electromagnet powered by a Tektronix/Keithley 2460 source-measure unit, generating a highly stable and uniform magnetic field. This field was measured with a four-digit gauss meter to be approximately 115 mT, with cross-sectional variations under 1%. Each sensor on the PCB recorded both positive and negative field measurements (i.e., aligned and anti-aligned to the same field). These high and low-field data points, along with the zero-field

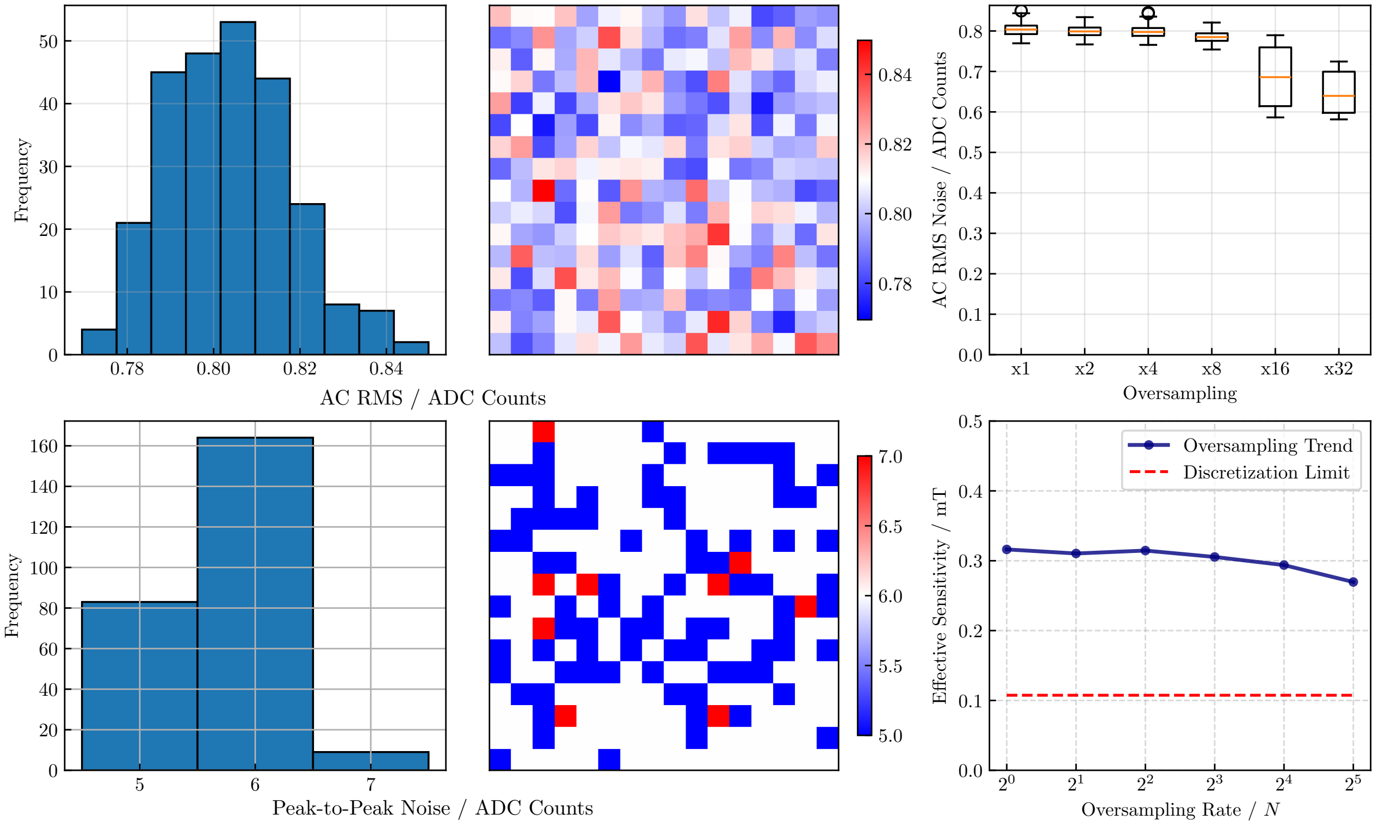
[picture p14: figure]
Frequency; Oversampling; AC RMS Noise / ADC Counts; Oversampling Rate / N; Eective Sensitivity / mT; Oversampling Trend Discretization Limit; Peak-to-Peak Noise / ADC Counts; AC RMS / ADC Counts

Fig. 13. Peak-to-peak and AC RMS noise data and spatial distributions, AC RMS noise boxplots as a function of hardware oversampling window size, and effective sensitivity as a function of hardware oversampling window size.

average, were binned into histograms and used to perform a
three-point linear regression, with the resulting sensitivities
shown in Fig. 14. This calibration focused on determining the linear sensitivity of each sensor, and not validating the sensor linearity that was already guaranteed by the manufacturer [19]. Both the linearity and DC offset constant show no significant or persistent geometric correlation across the sensor plane, which would be indicative of a misbehaving filter or some source of localized noise on the PCB, as shown in Fig. 14. While sensitive enough to meet the requirements set for the device, observed sensitivities were still generally below the quoted values from the sensors’ manufacturer [19], potentially indicating that the filters have a gain slightly but consistently higher than unity, which could be explained by capacitors generally erring on the side of being bellow the stated capacitance rather than above (although still within the quoted 5% tolerances).
C. Experimental Performance of Electronics
Using an oscilloscope with a logic analyzer add on, a full digital and analog capture of an acquisition event can be made simultaneously. Fig. 15 shows the full digital signal capture of the digital logic going to and from the micro-controller, running at a reduced sampling rate. This logic proves that everything is working as expected, and highlights where the parallelization provided by an FPGA could be used to dramatically increase performance. Timings could also be tightened to achieve higher a sampling rate by accounting for the time taken to move SPI results from the input buffer to memory, which would reduce the required programmed wait times between transactions. Similarly, Fig. 7 shows the experimental filter response of the final filter design, slightly improved over the prototype shown in Fig. 11. The filter settles slightly faster here with only a single Sallen-Key stage, at the cost of a more relaxed attenuation response in the frequency domain. The experimental filter is very close but still noticeably slower in settling than the LTspice simulation, which is likely due to either an overly optimistic spice model provided by the manufacture of the op-amp and/or multiplexer (either an overstated slew time or underquoted switching speed), or from the spice model not adequately modeling the effects of the ADC on the filter circuit (a lack of modeling of input capacitance, for example). Future iterations of the device should raise the pole frequency, fp, to combat this slower than expected performance.

IV. DISCUSSION
The scope of the 2D Hall array in this configuration is inherently limited to small, spherical tokamaks where the array dimensions can be reasonably compared to the toroidal region of interest while maintaining sufficient sensor granularity. This device offers small fusion endeavors a cost-effective alternative to the comprehensive field mapping solutions available to larger, more mature projects.
The device demonstrates significant pedagogical potential, serving as digital version of magnetic viewing film. It could

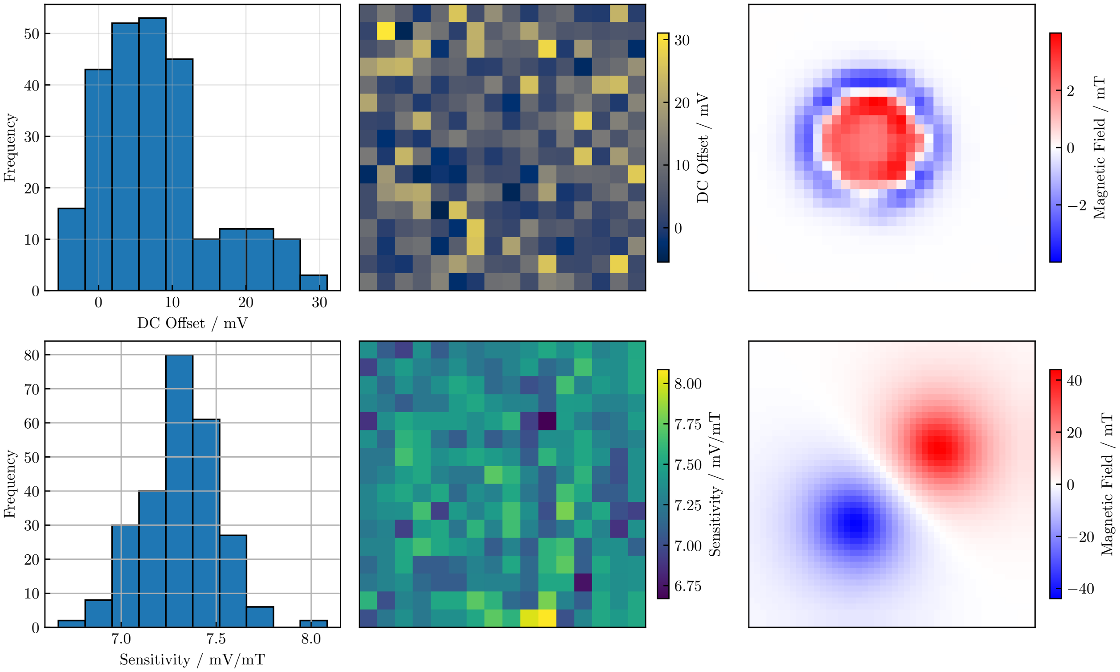
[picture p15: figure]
DC Oset / mV; Frequency; Sensitivity / mV/mT; Magnetic Field / mT

Fig. 14. Calibration results: DC offset with zero applied field (top); linear magnetic field sensitivity (bottom); preliminary imagery (right) of an Apple MagSafe charger and a very strong bar magnet, showing the use of bicubic interpolation. The manufacturer quotes an expected sensitivity of 7.5 mV/mT [19].

enhance undergraduate instruction in general physics and
introductory electromagnetism courses by enabling direct
observation of fundamental concepts, like the magnetic fields
produced by current-carrying wires. The visual and interactive nature of the device makes it particularly suitable for outreach activities, and AtomCraft will use it to attract new students recruits to the project and the University broadly, with the device expected to be presented to the general public at the upcoming UNSW Open Day in early September 2025.

The array’s sensitivity, dynamic range and low noise floor open possibilities for its use as a plasma diagnostic tool in SOUTH for monitoring poloidal fields (where the intrusion into the plasma is not as prohibitive to tokamak operations), as demonstrated previously [9]. However, its application in larger tokamaks like ITER or commercial reactors faces challenges. In addition to the aforementioned geometric limitations, its reliance on commercial sensors restricts operation in highradiation environments, a problem avoided by ITER’s custom bismuth sensors [6], for example. Additionally, the multiplexed topology introduces aliasing risks for high-frequency plasma instabilities above 20 kHz. Future iterations could explore custom sensors or more exotic analog filtering and ADC configurations to address these limitations, potentially expanding the device’s utility to both engineering validation and plasma physics in small-to-medium size fusion devices.

A. Immediate Future Developments
The immediate priority for future development of this work is the continued design of an FPGA digital control board which can ‘slot in’ to replace the Teensy microcontroller. A breakout board to adapt the connector that comes out of the device to interface with a Pynq Z2 FPGA development board has already been designed, manufactured and assembled, and some preliminary FPGA development has already commenced. The better than expected performance of the microcontroller implementation have lessened the requirement to have the FPGA ready as soon as possible, but it is still required to take full advantage of the bandwidth on offer and is therefore still a future goal.
B. Presentation at SOFE 2025
While presenting this work at the Symposium on Fusion Engineering 2025, on the MIT Campus in Cambridge, MA, there were a few attendees who had suggestions or observations about potential applications of the device, these are included here as potential future developments.
One attendee from the MIT Plasma Science and Fusion Center (PSFC) asked about the prospects of using a similar device submerged in liquid nitrogen for the monitoring of superconducting magnets, within the context of MIT PSFC’s new superconducting magnet test facility [24] which is being used for the development of new tokamaks and stellarators

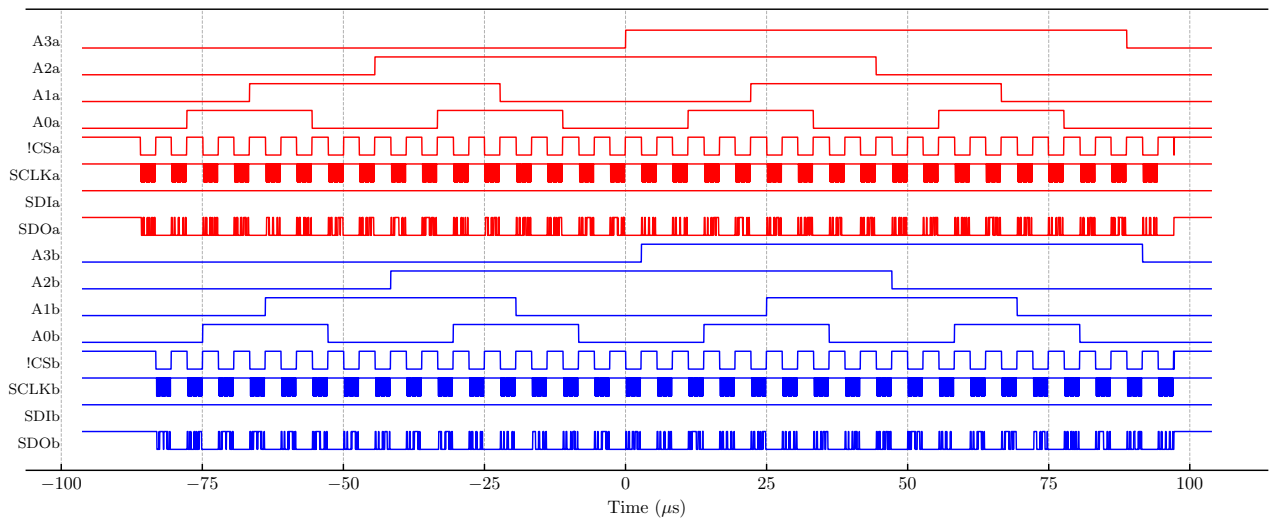
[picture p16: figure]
Time (µs); !CSa; SCLKa; SDIa; SDOa; !CSb; SCLKb; SDIb; SDOb

Fig. 15. Experimental capture of the digital logic behind a single ‘image’ taken using the digital channels of an oscilloscope (this data was recorded at the exact same time as that of Fig. 7). Compare this with the code shown in Listing 1 in the supporting material to get a better idea of what each SPI transaction is for. Note the very quick ‘reset sequencer’ pulse on the chip select lines towards the very end of the data.

like Commonwealth Fusion Systems’ (SP)ARC reactors [25]
and Type One Energy’s FPP [26].
This application is extremely novel and innovative, but
equally challenging and technically demanding. The device would need to be redesigned so that only the Hall sensors— and not any of the supporting electronics—get dipped into the liquid nitrogen, with all analog processing and data acquisition happening externally, and different, high-field Hall sensors would also need to be used. Getting the Hall sensors to function while submerged in liquid nitrogen initially seems like a technical hurdle, with the datasheet discouraging operation outside of a quite restrictive thermal envelope [19], but another attendee from OpenStar technologies (a New Zealandbased levitating dipole fusion company [27] that AtomCraft collaborates with) remarked that they semi-regularly use offthe-shelf Hall effect sensors in similar conditions with full functionality, even when operating well outside of datasheet specifications.
Another attendee from the Princeton Plasma Physics Laboratory (PPPL) asked about the possibility of using a similar array for liquid metal tomography and identified an extremely high dynamic range as critical for this application, with the ability to distinguish small fields (mT range) in the pretense of a very large background (multiple T) the key requirement. An array of Hall sensors is suited to this task, but likely custom sensors would be needed, potentially with a tuned analog bias current applied to cancel out the passive magnet field, as the dynamic range requirements are otherwise so extreme.
C. Future Collaboration with SMART Tokamak in Seville After networking and exchanging contact details at SOFE 2025, a preliminary collaboration between these authors and the SMART Tokamak team—a collaboration between the University of Seville and the PPPL [4]—has begun with the goal of using a small set of similar devices to monitor and control the alignment of coils during the re-assembly of the SMART tokamak, which is happening until late October 2025. The preliminary concept is to apply a ‘small’ DC currents to the tokamak’s magnetic coils, and then use a set of about six arrays in key locations to confirm that all the fields are adding as constructively as possible as each coil is moved into position and secured. The first author is expected to visit SMART in Seville in late 2025 to assist with this work, and communication is ongoing between the two teams currently.
V. CONCLUSION
This paper has presented the design, performance, and preliminary results of a high-resolution 2D Hall effect array device built to aid in the research and development of a small spherical tokamak. By functioning as a magnetic field camera, the arrays can image the toroidal fields within the region of plasma confinement and de-risk engineering efforts by verifying that generated magnetic fields match multiphysics simulations. The device demonstrates a high effective resolution of 0.32 mT, an average AC RMS noise floor of 0.086 mT and a dynamic range exceeding ±150 mT. The completed system provides a practical, cost-effective solution for magnetic field mapping in resource-constrained environments while offering substantial educational value. The low noise performance achieved with commercial components establishes a new benchmark for future developments of similar systems, in fusion engineering and beyond.
Following a positive reception from the fusion community at SOFE2025, this device will be used in the assembly of SOUTH in the medium-term future—up until late 2026—and will be applied shortly to the assembly and commissioning of the SMART tokamak, in preparation for its second experimental campaign envisioned to commence in late 2025/early 2026.

ACKNOWLEDGMENTS
We would like to thank all the students and academics of AtomCraft – especially Patrick Burr and Ed Obbard – for providing the context for this research, as well as enabling our access to facilities. Thank you to the lab staff in the mechatronics research laboratory and physics higher-years teaching laboratory for the use of their facilities, guidance and help with fabrication and testing.
Presentation of this work at SOFE2025 was funded by the Sir William Tyree foundation through the UNSW Nuclear Innovation Center Travel Award.

REFERENCES
[1] AtomCraft collaboration, private internal communications, 2024–2025.
[2] S. K. Nielsen et al., “First results from the NORTH tokamak,” Fusion Engineering and Design, vol. 166, p. 112288, May 2021, doi: 10.1016/j.fusengdes.2021.112288.
[3] A. Sykes et al., “The ST25 Tokamak for rapid technological development,” in 2013 IEEE 25th Symposium on Fusion Engineering (SOFE), Jun. 2013, pp. 1–4. doi: 10.1109/SOFE.2013.6635330.
[4] M. Agredano-Torres et al., “Coils and power supplies design for the SMART tokamak,” Fusion Engineering and Design, vol. 168, p. 112683, Jul. 2021, doi: 10.1016/j.fusengdes.2021.112683.
[5] M. Hasegawa et al., “Current status and prospect of plasma control system for steady-state operation on QUEST,” Fusion Engineering and Design, vol. 112, pp. 699–702, Nov. 2016, doi: 10.1016/j.fusengdes.2016.04.016.
[6] R. Chavan et al., “The magnetics diagnostic set for ITER,” Fusion Engineering and Design, vol. 84, no. 2, pp. 295–299, Jun. 2009, doi: 10.1016/j.fusengdes.2008.12.103.
[7] X. Wu, H. Huang, L. Peng, Y. Huang, and Y. Wang, “Algorithm Research on the Conductor Eccentricity of a Circular Dot Matrix Hall High Current Sensor for ITER,” IEEE Transactions on Plasma Science, vol. 50, no. 6, pp. 1962–1970, Jun. 2022, doi: 10.1109/TPS.2022.3173286.
[8] N. Marconato, E. Sartori, and G. Serianni, “Numerical and Experimental Assessment of the New Magnetic Field Configuration in SPIDER,” IEEE Transactions on Plasma Science, vol. 50, no. 11, pp. 3884–3889, Nov. 2022, doi: 10.1109/TPS.2022.3167859.
[9] B. A. Stevenson, S. F. Knowlton, G. J. Hartwell, J. D. Hanson, and D.
A. Maurer, “Hall probe measurements of the poloidal magnetic field in Compact Toroidal Hybrid plasmas,” Review of Scientific Instruments, vol. 85, no. 9, p. 093502, Sep. 2014, doi: 10.1063/1.4894209.
[10] I. Duran, O. Hronov ˇ | a, J. St ´ | ockel, J. Sentkerestiov ¨ | a, and J. Havlicek, ´
“Magnetic measurements using array of integrated Hall sensors on the CASTOR tokamak,” Review of Scientific Instruments, vol. 79, no. 10, p. 10F123, Oct. 2008, doi: 10.1063/1.2971209.
[11] I. Duran, S. Entler, M. Kohout, M. Ko ˇ | can, and G. Vayakis, “High ˇ
magnetic field test of bismuth Hall sensors for ITER steady state magnetic diagnostic,” Review of Scientific Instruments, vol. 87, no. 11, p. 11D446, Oct. 2016, doi: 10.1063/1.4964435.
[12] K. Hanada et al., “Overview of recent progress on steady state operation of all-metal plasma facing wall device QUEST,” Nuclear Materials and Energy, vol. 27, p. 101013, Jun. 2021, doi: 10.1016/j.nme.2021.101013.
[13] P. Jansen, “A Third, High-Speed Magnetic Imager Tile,” Hackerday.io, Feb. 12, 2018. [Online]. Available: https://hackaday.io/project/18518-iteration-8/log/91551-a-third-high-speed-magnetic-imager-tile. Accessed: Oct. 30, 2024.
[14] R. H. Liang, K. Y. Cheng, C. H. Su, C. T. Weng, B. Y. Chen, and D.
N. Yang, “Gausssense: attachable stylus sensing using magnetic sensor grid,” in Proceedings of the 25th annual ACM Symposium on User Interface Software and Technology, Cambridge, MA, Oct. 2012. doi: 10.1145/2380116.2380157.
[15] P. Jansen, “A Magnetic Imager Tile,” Hackerday.io, Aug. 29, 2017. [Online]. Available: https://hackaday.io/project/18518-iteration-8/log/64376-a-magnetic-imager-tile. Accessed: Oct. 30, 2024.
[16] “Apple introduces next-generation iPad Pro, supercharged by the M2 chip,” Apple Newsroom (Australia). Accessed: Nov. 06, 2024. [Online]. Available: https://www.apple.com/au/newsroom/2022/10/apple-introduces-next-generation-ipad-pro-supercharged-by-the-m2-chip/
[17] C.-W. Liang, E. Balaban, E. Ahmad, Z. Zhang, J. Sexton, and M. Missous, “A real time high sensitivity high spatial resolution quantum well hall effect magnetovision camera,” Sensors and Actuators A: Physical, vol. 265, pp. 127–137, 01 2017, doi: 10.1016/j.sna.2017.08.035.
[18] J. Cai, T. Zhou, Y. Xu, and X. Zhu, “A High-Resolution Magnetic Field Imaging System Based on the Unpackaged Hall Element Array,” Applied Sciences, vol. 14, no. 13, Art. no. 13, Jan. 2024, doi: 10.3390/app14135788.
[19] Texas Instruments, “Ratiometric Linear Hall Effect Sensor,” DRV5055 datasheet, Jan. 2018 [Revised Apr. 2021].
[20] Analog Devices, “Single-Ended Input, Quad, Simultaneous Sampling, 16-Bit/14-Bit/12-Bit, SAR ADC,” AD7386-4/AD7387-4/AD7388-4 datasheet, Oct. 2023.
[21] P. Horowitz and W. Hill, The Art of Electronics, 3rd ed. Cambridge, U.K.: Cambridge Univ. Press, 2015, p. 1028.
[22] P. Stoffregen, “Teensy 4.1 Development Board,” PJRC, 2020. [Online]. Available: https://www.pjrc.com/store/teensy41.html
[23] Texas Instruments, “High-Accuracy, Automotive-Grade, Low-Noise, LDO Voltage Regulator,” TPS7A52-Q1 2-A datasheet, Sept. 2017 [Revised June 2018].
[24] T. Golfinopoulos et al., “The superconducting magnet test facility at the MIT Plasma Science and Fusion Center,” poster presented at: Symposium on Fusion Engineering, Cambridge, MA, USA, Jun. 2025. [MIT Plasma Science and Fusion Center; MIT Bates Research and Engineering Center; Commonwealth Fusion Systems]
[25] A. Creely et al., “Design progress toward the ARC fusion power plant,” presented at: Symposium on Fusion Engineering, Cambridge, MA, USA, Jun. 2025. [Commonwealth Fusion Systems]
[26] R. Ibekwe, “Overview of Magnet Zero,” presented at: Symposium on Fusion Engineering, Cambridge, MA, USA, Jun. 2025. [Type One Energy, Inc.]
[27] R. Mataira et al., “Modularity and iteration in the levitated dipole: Experiences from OpenStar Technologies,” presented at: Symposium on Fusion Engineering, Cambridge, MA, USA, Jun. 2025. [OpenStar Technologies]

Samuel Shelton is currently studying for the B.Sc. in physics and chemistry and the B.E. (Hons.) in aerospace engineering at the University of New South Wales, Sydney, Australia.
He has been involved in the AtomCraft project since May 2024 and has served as diagnostics team lead, designing the diagnostics systems architecture for the upcoming SOUTH tokamak. He has extensive undergraduate research experience in both mechanical engineering and physics, in both industrial and academic settings.
He was been awarded the UNSW Nuclear Innovation Centre and Tyree Foundation travel grant, as well as the Gates Cambridge Scholarship for doctoral study commencing in October 2025.

Will Midgley received the B.Sc. degree in computer science and the B.Eng. degree (Hons.) in mechatronics from The University of Melbourne, Australia, in 2008, and the Ph.D. degree from Cambridge University, U.K., in 2013.
From 2013 to 2014, he was a Research Associate at Cambridge University. Then, he worked at Mitsubishi Heavy Industries, Japan, from 2015 to 2017. Since 2022, he has been a Senior Lecturer in robotics and mechatronics at UNSW Sydney, Australia. His previous work includes optimal control of electric machines to reduce energy consumption and torque ripple as part of the Virtual Vehicle Integration and Development (ViVID) project and optimization of electrification of rail routes to reduce carbon dioxide emissions and energy usage. His current work focuses on applying mechatronics, control engineering, and machine learning to transportation systems to reduce energy consumption and carbon dioxide emissions.
Dr Midley is the mechatronics academic lead for AtomCraft.

SUPPLEMENTARY MATERIALS
A. Videos of Device in Operation
Essential Viewing: View the device in operation on YouTube https://youtu.be/sB7mTB tMe0. (https://youtu.be/sB7mTB_tMe0)
B. Schematics & Other Files
The full device schematics and Altium PCB files are hosted on GitHub at https://github.com/Sam-js2/BEThesis, as well as the poster that was presented at SOFE 2025 and the Thesis C conference presentation.
C. Microcontroller Code
The full code for the real-time interaction module (shown in the supporting video) can be found on GitHub at https: //github.com/Sam-js2/BEThesis. Some code is shown here, but some functions are only defined in the full codebase.

1 void setup() {

2
3 Serial.begin(115200);

4
5 | SPI.begin();
6 | SPI.beginTransaction(SPISettings(spiClock, MSBFIRST, SPI_MODE2));
7 | SPI1.begin();
8 | SPI1.beginTransaction(SPISettings(spiClock, MSBFIRST, SPI_MODE2));

9
10 delayMicroseconds(t_powerup) ;

11
12 | adcA.hardReset();
13 | adcB.hardReset();

14
15 | adcA.configADC();
16 | adcB.configADC();

17
18 | delayMicroseconds(cycleWait);
19 | }

20
21 void loop() {

22
23 | // Junk data out, these trigger measurements
24 | adcA.spiRead() | ;
25 | adcB.spiRead() | ;
26 | delayNanoseconds(wait1) | ;

27
28 for (int i = 0; i <= 15; i++) {

29
30 | // Read THEN multiplex
31 | adcA.spiRead(&txPacket.data[6*i + 0 ]) | ;
32 | adcA.setMUX(gray[i+1]) | ;
33 | adcB.spiRead(&txPacket.data[6*i + 96]) | ;
34 | adcB.setMUX(gray[i+1]) | ;

35
36 delayNanoseconds(wait2) ; // Filter settling

37
38 | adcA.spiRead(&txPacket.data[6*i + 3 ]) | ;
39 | adcB.spiRead(&txPacket.data[6*i + 99]) | ;
40 | // Pointers direct data to correct place in packet strut
41 | }

42
43 | transmit() | ;
44 | pulseBothCS() ; // Resets Sequencer
45 | delayMicroseconds(cycleWait) ; // Spacing between captures
46 | }

Listing 1. C++ setup function and main loop for real-time operation on the Teensy 4.1.

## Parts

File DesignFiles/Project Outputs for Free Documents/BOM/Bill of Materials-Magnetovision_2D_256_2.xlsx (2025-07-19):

Comment | Description | Designator | Quantity
100n | Capacitor SMD 0603 | C1_B1, C1_B2, C1_B3, C1_B4, C1_B5, C1_B6, C1_B7, C1_B8, C1_B9, C1_B10, C1_B11, C1_B12, C1_B13, C1_B14, C1_B15, C1_B16, C2_B1, C2_B2, C2_B3, C2_B4, C2_B5, C2_B6, C2_B7, C2_B8, C2_B9, C2_B10, C2_B11, C2_B12, C2_B13, C2_B14, C2_B15, C2_B16, C3_B1, C3_B2, C3_B3, C3_B4, C3_B5, C3_B6, C3_B7, C3_B8, C3_B9, C3_B10, C3_B11, C3_B12, C3_B13, C3_B14, C3_B15, C3_B16, C4_B1, C4_B2, C4_B3, C4_B4, C4_B5, C4_B6, C4_B7, C4_B8, C4_B9, C4_B10, C4_B11, C4_B12, C4_B13, C4_B14, C4_B15, C4_B16, C5_B1, C5_B2, C5_B3, C5_B4, C5_B5, C5_B6, C5_B7, C5_B8, C5_B9, C5_B10, C5_B11, C5_B12, C5_B13, C5_B14, C5_B15, C5_B16, C6_B1, C6_B2, C6_B3, C6_B4, C6_B5, C6_B6, C6_B7, C6_B8, C6_B9, C6_B10, C6_B11, C6_B12, C6_B13, C6_B14, C6_B15, C6_B16, C7_B1, C7_B2, C7_B3, C7_B4, C7_B5, C7_B6, C7_B7, C7_B8, C7_B9, C7_B10, C7_B11, C7_B12, C7_B13, C7_B14, C7_B15, C7_B16, C8_B1, C8_B2, C8_B3, C8_B4, C8_B5, C8_B6, C8_B7, C8_B8, C8_B9, C8_B10, C8_B11, C8_B12, C8_B13, C8_B14, C8_B15, C8_B16, C9_B1, C9_B2, C9_B3, C9_B4, C9_B5, C9_B6, C9_B7, C9_B8, C9_B9, C9_B10, C9_B11, C9_B12, C9_B13, C9_B14, C9_B15, C9_B16, C10_B1, C10_B2, C10_B3, C10_B4, C10_B5, C10_B6, C10_B7, C10_B8, C10_B9, C10_B10, C10_B11, C10_B12, C10_B13, C10_B14, C10_B15, C10_B16, C11_B1, C11_B2, C11_B3, C11_B4, C11_B5, C11_B6, C11_B7, C11_B8, C11_B9, C11_B10, C11_B11, C11_B12, C11_B13, C11_B14, C11_B15, C11_B16, C12_B1, C12_B2, C12_B3, C12_B4, C12_B5, C12_B6, C12_B7, C12_B8, C12_B9, C12_B10, C12_B11, C12_B12, C12_B13, C12_B14, C12_B15, C12_B16, C13_B1, C13_B2, C13_B3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 | 304
1u | Capacitor SMD 0603 | C18_ADC1, C18_ADC2, C19_ADC1, C19_ADC2, C20_ADC1, C20_ADC2, C22_ADC1, C22_ADC2, C23_ADC1, C23_ADC2, C24_ADC1, C24_ADC2, C26, C28, C30, C32, C34, C36 | 18
2u2 24V | Capacitor SMD 0805 | C37, C38 | 2
22u | Capacitor SMD 0805 | C39, C46, C47 | 3
47u | 865080543009 Alum. Electrolytic Cap 47µF 35V 6.3mmV-Chip WCAP-ASLI; Lifetime 2000h +105°C | C41, C49, C50, C51, C52 | 5
10u | Capacitor SMD 0805 | C43, C44 | 2
47p | Capacitor SMD 0603 | C53_F11, C53_F12, C53_F13, C53_F14, C53_F15, C53_F16, C53_F17, C53_F18, C53_F19, C53_F110, C53_F111, C53_F112, C53_F113, C53_F114, C53_F115, C53_F116 | 16
30p | Capacitor SMD 0603 | C55_F11, C55_F12, C55_F13, C55_F14, C55_F15, C55_F16, C55_F17, C55_F18, C55_F19, C55_F110, C55_F111, C55_F112, C55_F113, C55_F114, C55_F115, C55_F116 | 16
330p | Capacitor SMD 0603 | C56_F11, C56_F12, C56_F21, C56_F22, C57_F11, C57_F12, C57_F21, C57_F22, C58_F11, C58_F12, C58_F21, C58_F22, C59_F11, C59_F12, C59_F21, C59_F22 | 16
SMA Shottky | Diode Schottky SMD SMA (DO-214AA) | D1 | 1
LED_0603_GREEN | LED 0603 GREEN SMD | D2 | 1
AD7388-4 | Single-Ended Input, Quad, Simultaneous Sampling, 16-Bit, SAR ADC | IC1_ADC1, IC1_ADC2 | 2
TPS7A5201QRGRRQ1 | Integrated Circuit | IC2 | 1
SYZYGY STD Peripheral |  | J1 | 1
39-28-1063 | 4.2 mm Pitch Mini-Fit Jr.Power Connector, Vertical, Through Hole, 6 Circuits, -40 to 105 degC, RoHS, Bag | J2 | 1
4.7u |  | L1, L2 | 2
DRV5055A4 | Hall Effect Sensor, 176mT Min, -1-1mA, Plastic/epoxy, Rectangular, 3 Pin, Surface Mount, DRV5055A4QDBZR | MAG1_B1, MAG1_B2, MAG1_B3, MAG1_B4, MAG1_B5, MAG1_B6, MAG1_B7, MAG1_B8, MAG1_B9, MAG1_B10, MAG1_B11, MAG1_B12, MAG1_B13, MAG1_B14, MAG1_B15, MAG1_B16, MAG2_B1, MAG2_B2, MAG2_B3, MAG2_B4, MAG2_B5, MAG2_B6, MAG2_B7, MAG2_B8, MAG2_B9, MAG2_B10, MAG2_B11, MAG2_B12, MAG2_B13, MAG2_B14, MAG2_B15, MAG2_B16, MAG3_B1, MAG3_B2, MAG3_B3, MAG3_B4, MAG3_B5, MAG3_B6, MAG3_B7, MAG3_B8, MAG3_B9, MAG3_B10, MAG3_B11, MAG3_B12, MAG3_B13, MAG3_B14, MAG3_B15, MAG3_B16, MAG4_B1, MAG4_B2, MAG4_B3, MAG4_B4, MAG4_B5, MAG4_B6, MAG4_B7, MAG4_B8, MAG4_B9, MAG4_B10, MAG4_B11, MAG4_B12, MAG4_B13, MAG4_B14, MAG4_B15, MAG4_B16, MAG5_B1, MAG5_B2, MAG5_B3, MAG5_B4, MAG5_B5, MAG5_B6, MAG5_B7, MAG5_B8, MAG5_B9, MAG5_B10, MAG5_B11, MAG5_B12, MAG5_B13, MAG5_B14, MAG5_B15, MAG5_B16, MAG6_B1, MAG6_B2, MAG6_B3, MAG6_B4, MAG6_B5, MAG6_B6, MAG6_B7, MAG6_B8, MAG6_B9, MAG6_B10, MAG6_B11, MAG6_B12, MAG6_B13, MAG6_B14, MAG6_B15, MAG6_B16, MAG7_B1, MAG7_B2, MAG7_B3, MAG7_B4, MAG7_B5, MAG7_B6, MAG7_B7, MAG7_B8, MAG7_B9, MAG7_B10, MAG7_B11, MAG7_B12, MAG7_B13, MAG7_B14, MAG7_B15, MAG7_B16, MAG8_B1, MAG8_B2, MAG8_B3, MAG8_B4, MAG8_B5, MAG8_B6, MAG8_B7, MAG8_B8, MAG8_B9, MAG8_B10, MAG8_B11, MAG8_B12, MAG8_B13, MAG8_B14, MAG8_B15, MAG8_B16, MAG9_B1, MAG9_B2, MAG9_B3, MAG9_B4, MAG9_B5, MAG9_B6, MAG9_B7, MAG9_B8, MAG9_B9, MAG9_B10, MAG9_B11, MAG9_B12, MAG9_B13, MAG9_B14, MAG9_B15, MAG9_B16, MAG10_B1, MAG10_B2, MAG10_B3, MAG10_B4, MAG10_B5, MAG10_B6, MAG10_B7, MAG10_B8, MAG10_B9, MAG10_B10, MAG10_B11, MAG10_B12, MAG10_B13, MAG10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 | 256
3670250 | 3670250 Shield Cabinet Frame, 25Mm X 21Mm Rohs Compliant: Yes | MP1_ADC1, MP1_ADC2 | 2
100R | Resistor SMD 0603 | R1_ADC1, R1_ADC2, R2_ADC1, R2_ADC2, R3_ADC1, R3_ADC2, R4_ADC1, R4_ADC2 | 8
33R | Resistor SMD 0603 | R5, R6, R7, R8, R15_F11, R15_F12, R15_F21, R15_F22, R16_F11, R16_F12, R16_F21, R16_F22, R17_F11, R17_F12, R17_F21, R17_F22, R18_F11, R18_F12, R18_F21, R18_F22 | 20
11.8k 1% | Resistor SMD 0603 | R9, R12 | 2
1k | Resistor SMD 0603 | R10 | 1
3.74k 1% | Resistor SMD 0603 | R11 | 1
2.21k | Resistor SMD 0603 | R13_F11, R13_F12, R13_F13, R13_F14, R13_F15, R13_F16, R13_F17, R13_F18, R13_F19, R13_F110, R13_F111, R13_F112, R13_F113, R13_F114, R13_F115, R13_F116 | 16
5k | Resistor SMD 0603 | R14_F11, R14_F12, R14_F13, R14_F14, R14_F15, R14_F16, R14_F17, R14_F18, R14_F19, R14_F110, R14_F111, R14_F112, R14_F113, R14_F114, R14_F115, R14_F116 | 16
TXV0108QWRGYRQ1 | Integrated Circuit | U1, U2, U3 | 3
ADA4807-2ARMZ-R7 | IC OPAMP VFB 2 CIRCUIT 8MSOP | U4_F11, U4_F12, U4_F13, U4_F14, U4_F15, U4_F16, U4_F17, U4_F18, U4_F19, U4_F110, U4_F111, U4_F112, U4_F113, U4_F114, U4_F115, U4_F116 | 16
ADG706BRUZ | 1.8 to 5.5 V / 2.5 V, CMOS Low-Voltage 2.5 Ohm, 16-Channel Multiplexer, -40 to 85 degC, 28-pin SOP (RU-28), Reel | U5_B1, U5_B2, U5_B3, U5_B4, U5_B5, U5_B6, U5_B7, U5_B8, U5_B9, U5_B10, U5_B11, U5_B12, U5_B13, U5_B14, U5_B15, U5_B16 | 16
ADA4807-4 | IC OPAMP VFB 4 CIRCUIT 14TSSOP | U6_F11, U6_F12, U6_F21, U6_F22 | 4

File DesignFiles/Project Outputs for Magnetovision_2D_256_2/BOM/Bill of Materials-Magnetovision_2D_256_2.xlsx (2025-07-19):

Comment | Description | Designator | Footprint | Quantity
100n | Capacitor SMD 0603 | C1_B1, C1_B2, C1_B3, C1_B4, C1_B5, C1_B6, C1_B7, C1_B8, C1_B9, C1_B10, C1_B11, C1_B12, C1_B13, C1_B14, C1_B15, C1_B16, C2_B1, C2_B2, C2_B3, C2_B4, C2_B5, C2_B6, C2_B7, C2_B8, C2_B9, C2_B10, C2_B11, C2_B12, C2_B13, C2_B14, C2_B15, C2_B16, C3_B1, C3_B2, C3_B3, C3_B4, C3_B5, C3_B6, C3_B7, C3_B8, C3_B9, C3_B10, C3_B11, C3_B12, C3_B13, C3_B14, C3_B15, C3_B16, C4_B1, C4_B2, C4_B3, C4_B4, C4_B5, C4_B6, C4_B7, C4_B8, C4_B9, C4_B10, C4_B11, C4_B12, C4_B13, C4_B14, C4_B15, C4_B16, C5_B1, C5_B2, C5_B3, C5_B4, C5_B5, C5_B6, C5_B7, C5_B8, C5_B9, C5_B10, C5_B11, C5_B12, C5_B13, C5_B14, C5_B15, C5_B16, C6_B1, C6_B2, C6_B3, C6_B4, C6_B5, C6_B6, C6_B7, C6_B8, C6_B9, C6_B10, C6_B11, C6_B12, C6_B13, C6_B14, C6_B15, C6_B16, C7_B1, C7_B2, C7_B3, C7_B4, C7_B5, C7_B6, C7_B7, C7_B8, C7_B9, C7_B10, C7_B11, C7_B12, C7_B13, C7_B14, C7_B15, C7_B16, C8_B1, C8_B2, C8_B3, C8_B4, C8_B5, C8_B6, C8_B7, C8_B8, C8_B9, C8_B10, C8_B11, C8_B12, C8_B13, C8_B14, C8_B15, C8_B16, C9_B1, C9_B2, C9_B3, C9_B4, C9_B5, C9_B6, C9_B7, C9_B8, C9_B9, C9_B10, C9_B11, C9_B12, C9_B13, C9_B14, C9_B15, C9_B16, C10_B1, C10_B2, C10_B3, C10_B4, C10_B5, C10_B6, C10_B7, C10_B8, C10_B9, C10_B10, C10_B11, C10_B12, C10_B13, C10_B14, C10_B15, C10_B16, C11_B1, C11_B2, C11_B3, C11_B4, C11_B5, C11_B6, C11_B7, C11_B8, C11_B9, C11_B10, C11_B11, C11_B12, C11_B13, C11_B14, C11_B15, C11_B16, C12_B1, C12_B2, C12_B3, C12_B4, C12_B5, C12_B6, C12_B7, C12_B8, C12_B9, C12_B10, C12_B11, C12_B12, C12_B13, C12_B14, C12_B15, C12_B16, C13_B1, C13_B2, C13_B3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 | CAP_0603 | 304
1u | Capacitor SMD 0603 | C18_ADC1, C18_ADC2, C19_ADC1, C19_ADC2, C20_ADC1, C20_ADC2, C22_ADC1, C22_ADC2, C23_ADC1, C23_ADC2, C24_ADC1, C24_ADC2, C26, C28, C30, C32, C34, C36 | CAP_0603 | 18
2u2 24V | Capacitor SMD 0805 | C37, C38 | CAP_0805 | 2
22u | Capacitor SMD 0805 | C39, C43, C44, C46, C47 | CAP_0805 | 5
47u | 865080543009 Alum. Electrolytic Cap 47µF 35V 6.3mmV-Chip WCAP-ASLI; Lifetime 2000h +105°C | C41, C49, C50, C51, C52 | WCAP-ASLI_D6.3H5.5 | 5
47p | Capacitor SMD 0603 | C53_F11, C53_F12, C53_F13, C53_F14, C53_F15, C53_F16, C53_F17, C53_F18, C53_F19, C53_F110, C53_F111, C53_F112, C53_F113, C53_F114, C53_F115, C53_F116 | CAP_0603 | 16
30p | Capacitor SMD 0603 | C55_F11, C55_F12, C55_F13, C55_F14, C55_F15, C55_F16, C55_F17, C55_F18, C55_F19, C55_F110, C55_F111, C55_F112, C55_F113, C55_F114, C55_F115, C55_F116 | CAP_0603 | 16
330p | Capacitor SMD 0603 | C56_F11, C56_F12, C56_F21, C56_F22, C57_F11, C57_F12, C57_F21, C57_F22, C58_F11, C58_F12, C58_F21, C58_F22, C59_F11, C59_F12, C59_F21, C59_F22 | CAP_0603 | 16
SMA Shottky | Diode Schottky SMD SMA (DO-214AA) | D1 | DO-214AC-2 (SMA) | 1
LED_0603_GREEN | LED 0603 GREEN SMD | D2 | LED_0603_GREEN | 1
AD7388-4 | Single-Ended Input, Quad, Simultaneous Sampling, 16-Bit, SAR ADC | IC1_ADC1, IC1_ADC2 | QFN50P400X400X60-25N-D | 2
TPS7A5201QRGRRQ1 | Integrated Circuit | IC2 | QFN50P350X350X100-21N-D | 1
QTE-020-01-L-D-A-K-TR | Board to Board & Mezzanine Connectors Q Strip High-Speed Ground Plane Header, 0.80mm Pitch | J1 | FP-QTE-020-01-L-D-A-K-TR_MFG | 1
43045-0201 | Connector | J2 | 43045-02YY | 1
4.7u |  | L1, L2 | WE-LHMI_7030 | 2
DRV5055A4 | Hall Effect Sensor, 176mT Min, -1-1mA, Plastic/epoxy, Rectangular, 3 Pin, Surface Mount, DRV5055A4QDBZR | MAG1_B1, MAG1_B2, MAG1_B3, MAG1_B4, MAG1_B5, MAG1_B6, MAG1_B7, MAG1_B8, MAG1_B9, MAG1_B10, MAG1_B11, MAG1_B12, MAG1_B13, MAG1_B14, MAG1_B15, MAG1_B16, MAG2_B1, MAG2_B2, MAG2_B3, MAG2_B4, MAG2_B5, MAG2_B6, MAG2_B7, MAG2_B8, MAG2_B9, MAG2_B10, MAG2_B11, MAG2_B12, MAG2_B13, MAG2_B14, MAG2_B15, MAG2_B16, MAG3_B1, MAG3_B2, MAG3_B3, MAG3_B4, MAG3_B5, MAG3_B6, MAG3_B7, MAG3_B8, MAG3_B9, MAG3_B10, MAG3_B11, MAG3_B12, MAG3_B13, MAG3_B14, MAG3_B15, MAG3_B16, MAG4_B1, MAG4_B2, MAG4_B3, MAG4_B4, MAG4_B5, MAG4_B6, MAG4_B7, MAG4_B8, MAG4_B9, MAG4_B10, MAG4_B11, MAG4_B12, MAG4_B13, MAG4_B14, MAG4_B15, MAG4_B16, MAG5_B1, MAG5_B2, MAG5_B3, MAG5_B4, MAG5_B5, MAG5_B6, MAG5_B7, MAG5_B8, MAG5_B9, MAG5_B10, MAG5_B11, MAG5_B12, MAG5_B13, MAG5_B14, MAG5_B15, MAG5_B16, MAG6_B1, MAG6_B2, MAG6_B3, MAG6_B4, MAG6_B5, MAG6_B6, MAG6_B7, MAG6_B8, MAG6_B9, MAG6_B10, MAG6_B11, MAG6_B12, MAG6_B13, MAG6_B14, MAG6_B15, MAG6_B16, MAG7_B1, MAG7_B2, MAG7_B3, MAG7_B4, MAG7_B5, MAG7_B6, MAG7_B7, MAG7_B8, MAG7_B9, MAG7_B10, MAG7_B11, MAG7_B12, MAG7_B13, MAG7_B14, MAG7_B15, MAG7_B16, MAG8_B1, MAG8_B2, MAG8_B3, MAG8_B4, MAG8_B5, MAG8_B6, MAG8_B7, MAG8_B8, MAG8_B9, MAG8_B10, MAG8_B11, MAG8_B12, MAG8_B13, MAG8_B14, MAG8_B15, MAG8_B16, MAG9_B1, MAG9_B2, MAG9_B3, MAG9_B4, MAG9_B5, MAG9_B6, MAG9_B7, MAG9_B8, MAG9_B9, MAG9_B10, MAG9_B11, MAG9_B12, MAG9_B13, MAG9_B14, MAG9_B15, MAG9_B16, MAG10_B1, MAG10_B2, MAG10_B3, MAG10_B4, MAG10_B5, MAG10_B6, MAG10_B7, MAG10_B8, MAG10_B9, MAG10_B10, MAG10_B11, MAG10_B12, MAG10_B13, MAG10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 | SOT100P237X112-3N | 256
3670250 | 3670250 Shield Cabinet Frame, 25Mm X 21Mm Rohs Compliant: Yes | MP1_ADC1, MP1_ADC2 | 3670250 | 2
100R | Resistor SMD 0603 | R1_ADC1, R1_ADC2, R2_ADC1, R2_ADC2, R3_ADC1, R3_ADC2, R4_ADC1, R4_ADC2 | RES_0603 | 8
33R | Resistor SMD 0603 | R5, R6, R7, R8, R15_F11, R15_F12, R15_F21, R15_F22, R16_F11, R16_F12, R16_F21, R16_F22, R17_F11, R17_F12, R17_F21, R17_F22, R18_F11, R18_F12, R18_F21, R18_F22 | RES_0603 | 20
11.8k 1% | Resistor SMD 0603 | R9 | RES_0603 | 1
1k | Resistor SMD 0603 | R10 | RES_0603 | 1
3.74k 1% | Resistor SMD 0603 | R11 | RES_0603 | 1
11.8k | Resistor SMD 0603 | R12 | RES_0603 | 1
2.21k | Resistor SMD 0603 | R13_F11, R13_F12, R13_F13, R13_F14, R13_F15, R13_F16, R13_F17, R13_F18, R13_F19, R13_F110, R13_F111, R13_F112, R13_F113, R13_F114, R13_F115, R13_F116 | RES_0603 | 16
5k | Resistor SMD 0603 | R14_F11, R14_F12, R14_F13, R14_F14, R14_F15, R14_F16, R14_F17, R14_F18, R14_F19, R14_F110, R14_F111, R14_F112, R14_F113, R14_F114, R14_F115, R14_F116 | RES_0603 | 16
TXV0108QWRGYRQ1 | Integrated Circuit | U1, U2, U3 | TXV0108QWRGYRQ1 | 3
ADA4807-2ARMZ-R7 | IC OPAMP VFB 2 CIRCUIT 8MSOP | U4_F11, U4_F12, U4_F13, U4_F14, U4_F15, U4_F16, U4_F17, U4_F18, U4_F19, U4_F110, U4_F111, U4_F112, U4_F113, U4_F114, U4_F115, U4_F116 | FP-RM-8-IPC_A | 16
ADG706BRUZ | 1.8 to 5.5 V / 2.5 V, CMOS Low-Voltage 2.5 Ohm, 16-Channel Multiplexer, -40 to 85 degC, 28-pin SOP (RU-28), Reel | U5_B1, U5_B2, U5_B3, U5_B4, U5_B5, U5_B6, U5_B7, U5_B8, U5_B9, U5_B10, U5_B11, U5_B12, U5_B13, U5_B14, U5_B15, U5_B16 | ADI-RU-28_M | 16
ADA4807-4 | IC OPAMP VFB 4 CIRCUIT 14TSSOP | U6_F11, U6_F12, U6_F21, U6_F22 | FP-RU-14-IPC_A | 4

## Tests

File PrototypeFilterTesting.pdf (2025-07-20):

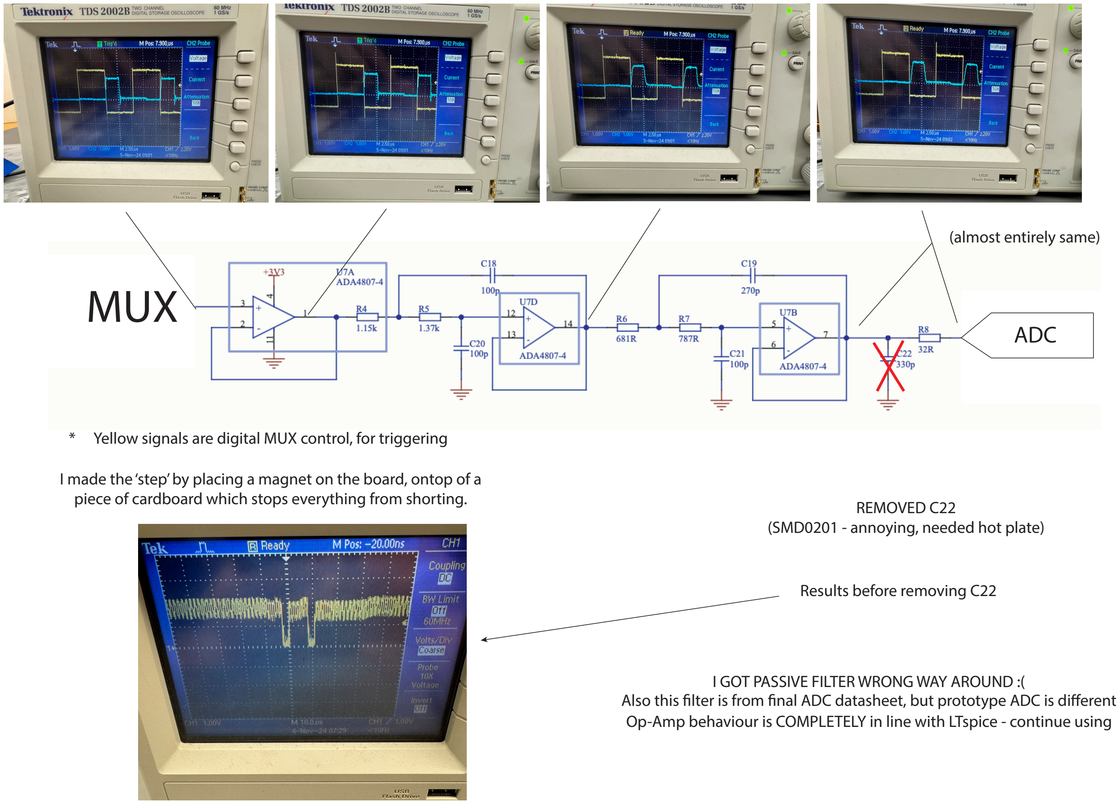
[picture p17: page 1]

# MUX

(almost entirely same)

## ADC

REMOVED C22
(SMD0201 - annoying, needed hot plate)

I GOT PASSIVE FILTER WRONG WAY AROUND :( Also this lter is from nal ADC datasheet, but prototype ADC is dierent Op-Amp behaviour is COMPLETELY in line with LTspice - continue using

* Yellow signals are digital MUX control, for triggering

I made the ‘step’ by placing a magnet on the board, ontop of a piece of cardboard which stops everything from shorting.

Results before removing C22

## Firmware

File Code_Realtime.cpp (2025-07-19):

/*
Code for running MAG256 from Teensy 4.1 Breakout Board, gets 6 kSPS
@samsh, UNSW
2024-25

24 MHz is the highest that can be reliably achieved without OC
At these speed, 16x oversampling requires EXTREMELY MINOR waits, barely slowing down sampling
At these speeds, 8140 us of wait gives 120.3 SPS.
Setting cycleWait to 50 uS achives 4 kHz without bany issue
The 'Transaction Window' is about 200 uS per 'sweep'
All of this was verified with an oscillosocpe

16x and 32x oversampling are misbehaving (wierd sequencing), so use 8x instead
I suspect this might be because an SPI transaction with no output to memory is much shorter;
It wouldn't use CPU clock cycles to move from buffer into memory
I need to invesitage futher... but pump up the waits and it still works fine

Interestingly, noise is bimodally distributed between X0 and X1 channels on 16 and 32x oversampling

NOTE: Write anywhere, but compile in Teensyduino. 600 MHz, FAST (no LTO) works best
*/

// Including standard libraries for SPI
#include <SPI.h>

// Things that you can adjust
constexpr int overSampleNum  = 8        ;   // Oversampling, can be 1 (i.e., none), 2, 4, 8, 16, 32
constexpr uint32_t spiClock  = 24e6     ;   // 24 MHz - highest the Teensy can do reliably, 48 MHz w/OC
constexpr uint32_t cycleWait = 150      ;    // Delay to limit cycle speed - in us - set to 15 ms for ~60 Hz - CRITICAL WHEN LARGE OVERSAMPLING!
#define SERIALDIAGNOSTICS 0                  // Gives some diagnostics over the serial port
#define CAPTURETIMINGS    0                  // Records crude timing information for packets

// Define the digital I/O Pins
// ADC A
#define CSa 10
#define A0a 9
#define A1a 8
#define A2a 7
#define A3a 6

// ADC B
#define CSb 38
#define A0b 25
#define A1b 24
#define A2b 40
#define A3b 41

// Non-default SPI Parameters
#define MISO1 39
#define MOSI1 26
#define SCK1  27

// Experimental multiplier -- SPI Bus efficiency, found using Scope
// Time taken = SPIefficiency*idealTime
#define SPIefficiency 1

// Defining Times
// Defining various wait times - in ns
constexpr uint32_t t_quiet    = 50     ;  // quiet time -- minimum is actually 20 but 50 ns is teensy minimum
constexpr uint32_t t_settle   = 1500    ;  // Acceptable minimum filter settling time
constexpr uint32_t t_isettle  = 500    ;  // Internal MUX settling time
constexpr uint32_t t_hardrst  = 800    ;  // Time to wait after hard reset before measurements
constexpr uint32_t t_softrst  = 250    ;  // Time to wait after soft reset before measurements
constexpr uint32_t t_powerup  = 10000  ;  // 10 ms

// Conversion Time
constexpr uint32_t calc_t_convert(int overSampleNum) {
  return 10 + 250*(overSampleNum-1);
}
constexpr uint32_t t_convert = calc_t_convert(overSampleNum);

// More Complex Wait Times
// Wait time between Internal ADC Mux'ed Inputs
constexpr uint32_t calc_wait1() {
    // 48 bits to transmit, SPI clock in Hz → convert to nanoseconds
    int32_t transmission_time = static_cast<int32_t>((48.0 / spiClock) * 1e9 * SPIefficiency);
    
    int32_t temp = (t_convert > t_isettle) ? 
        (static_cast<int32_t>(t_convert) - transmission_time) : 
        (static_cast<int32_t>(t_isettle) - transmission_time);
    
    return (temp > 0) ? static_cast<uint32_t>(temp) : 0;
}
constexpr uint32_t wait1 = calc_wait1();

constexpr uint32_t ioDelay = 500;

// Ensure there are only allowed oversampling values
static_assert(
  overSampleNum == 1 || overSampleNum == 2 || overSampleNum == 4 ||
  overSampleNum == 8 || overSampleNum == 16 || overSampleNum == 32,
  "Invalid oversampling value. Must be 1, 2, 4, 8, 16, or 32."
);

/**   Configuration Register 1
15  14    11  10  9   8     5   4   3   2   1   0
[1] [001] [0] [1] [0] [000] [0] [0] [0] [0] [1] [0]
R/W  adr  CH  SE  OS    #     CRC    AL  RES REF PMODE
*     no ALERT, no resolution boost, external reference, normal power mode             */
constexpr uint16_t setconfig1(int overSampleNum){
  switch(overSampleNum){
    case 1  : return 0x9402 ; // 1x  Sampling
    case 2  : return 0x9442 ; // 2x  Sampling
    case 4  : return 0x9482 ; // 4x  Sampling
    case 8  : return 0x94C2 ; // 8x  Sampling
    case 16 : return 0x9502 ; // 16x Sampling
    case 32 : return 0x9542 ; // 32x Sampling
    default : return 0xFFFF ; // fallback to make compiler happy
  }
}
constexpr uint16_t config1       = setconfig1(overSampleNum) ;
constexpr uint16_t config1_read  = 0x1000 ;

/**   Configuration Register 2
[1] [010] [00] [11] [00111100]
R/W  adr  res  SDP  RST 
*     1-wire SPI             */ 
constexpr uint16_t config2           = 0xA300  ;
constexpr uint16_t config2SoftReset  = 0xA33C  ;
constexpr uint16_t config2HardReset  = 0xA3FF  ;
constexpr uint16_t config2_read      = 0x2000  ;

// Lookup table Gray codes + Baud Rate
constexpr uint8_t gray[17]  = {0, 1, 3, 2, 6, 7, 5, 4, 12, 13, 15, 14, 10, 11, 9, 8, 0} ;
constexpr uint16_t zero     = 0xFFFF    ;   // What will be sent in 'empty' SPI transactions

// ADC Class
class ADC {
  private:
    uint8_t csPin;
    uint8_t a0Pin;
    uint8_t a1Pin;
    uint8_t a2Pin;
    uint8_t a3Pin;
    SPIClass* spi;
    
  public:
    // Constructor
    ADC(uint8_t cs, uint8_t a0, uint8_t a1, uint8_t a2, uint8_t a3, SPIClass* spiInterface) {
      csPin = cs;
      a0Pin = a0;
      a1Pin = a1;
      a2Pin = a2;
      a3Pin = a3;
      spi = spiInterface;
      
      // Initialize pins
      pinMode(csPin, OUTPUT);
      pinMode(a0Pin, OUTPUT);
      pinMode(a1Pin, OUTPUT);
      pinMode(a2Pin, OUTPUT);
      pinMode(a3Pin, OUTPUT);
      
      digitalWriteFast(csPin, HIGH);
      digitalWriteFast(a0Pin, LOW);
      digitalWriteFast(a1Pin, LOW);
      digitalWriteFast(a2Pin, LOW);
      digitalWriteFast(a3Pin, LOW);
    }
    
    // Set MUX
    void setMUX(uint8_t grayCode) {
      digitalWriteFast(a0Pin, grayCode & 0x01);
      digitalWriteFast(a1Pin, (grayCode >> 1) & 0x01);
      digitalWriteFast(a2Pin, (grayCode >> 2) & 0x01);
      digitalWriteFast(a3Pin, (grayCode >> 3) & 0x01);
    }

    void writeRegister(uint16_t reg) {
      digitalWriteFast(csPin, LOW);
      spi->transfer16(zero);
      digitalWriteFast(csPin, HIGH);

      delayNanoseconds(ioDelay);

      digitalWriteFast(csPin, LOW);
      spi->transfer16(reg);
      digitalWriteFast(csPin, HIGH);

      delayNanoseconds(ioDelay);
    }

    uint16_t readRegister(uint16_t reg) {
      digitalWriteFast(csPin, LOW);
      spi->transfer16(zero);
      digitalWriteFast(csPin, HIGH);

      delayNanoseconds(ioDelay);

      digitalWriteFast(csPin, LOW);
      spi->transfer16(reg);
      digitalWriteFast(csPin, HIGH);

      delayNanoseconds(ioDelay);

      digitalWriteFast(csPin, LOW);
      uint16_t result = spi->transfer16(zero);
      digitalWriteFast(csPin, HIGH);

      delayNanoseconds(ioDelay);

      digitalWriteFast(csPin, LOW);
      spi->transfer16(zero);
      digitalWriteFast(csPin, HIGH);

      delayNanoseconds(ioDelay);

      return result ;
    }

    void hardReset() {
      writeRegister(config2HardReset);
      delayNanoseconds(t_hardrst);
    }

    void softReset() {
      writeRegister(config2SoftReset);
      delayNanoseconds(t_softrst);
    }

    // Configure ADC
    void configADC() {
      const int MAX_RETRIES = 500; // maximum times to attempt rewriting

      // Validate config1
      bool config1Status = false;
      uint16_t config1Out;
      int retries = 0;
      while (!config1Status && retries < MAX_RETRIES) {
          writeRegister(config1);
          config1Out = readRegister(config1_read);
          // Masking sets address/rw to 0 (not expected back from ADC)
          if (config1Out == (config1 & 0x0FFF)) {
              config1Status = true;
          }
          retries++;
      }
      
      // Validate config2
      bool config2Status = false;
      uint16_t config2Out;
      retries = 0;  // Reset retry counter
      while (!config2Status && retries < MAX_RETRIES) { 
          writeRegister(config2);
          config2Out = readRegister(config2_read);
          // Masking sets address/rw to 0 (not expected back from ADC)
          if (config2Out == (config2 & 0x0FFF)) {
              config2Status = true;
          }
          retries++;
      }

      #if SERIALDIAGNOSTICS 
        Serial.println("ADC Diagnostics:");
        if (!config1Status) {
          Serial.print("ERROR: Config1 validation failed, last value: ");
          Serial.println(config1Out, HEX);
        }
        if (!config2Status) {
          Serial.print("ERROR: Config2 validation failed, last valule: ");
          Serial.println(config2Out, HEX);
        }
        if (config1Status && config2Status) {
          Serial.println("ADC configuration successful");
        }
      #endif
    }
    
    // Read Results
    void spiRead(uint16_t* dest) {
      digitalWriteFast(csPin, LOW);
      *dest       = spi->transfer16(zero);
      *(dest + 1) = spi->transfer16(zero);
      *(dest + 2) = spi->transfer16(zero);
      digitalWriteFast(csPin, HIGH);
    }
    void spiRead() {
      digitalWriteFast(csPin, LOW);
      spi->transfer16(zero);
      spi->transfer16(zero);
      spi->transfer16(zero);
      digitalWriteFast(csPin, HIGH);
    }
};

// Serial Packet Structure
struct serialPacket {
  // Sync Bytes
  uint8_t sync1 = 0xAA ;
  uint8_t sync2 = 0xBB ;
  uint8_t sync3 = 0xCC ;
  uint8_t sync4 = 0xDD ;

  // Counter - detect packet loss
  uint32_t count     = 0 ;
  uint32_t timeStamp = 0 ; // optionally used

  // Packet Information
  uint16_t dataSize =  384 ; // data size in uint16_t's
  uint8_t  version  = 0x01 ; // version 1
  uint8_t  flags    = 0x00 ; // unused for now 

  // Actual Data
  uint16_t data[192] = {0};

  // Spare space to pad to size -- can be used in future
  uint8_t spareData[104] = {0};

  // Space for CRC, unused for now
  uint32_t CRC = 0; 

  //End Sync Bytes
  uint8_t sync5 = 0xEE ;
  uint8_t sync6 = 0xFF ;
  uint8_t sync7 = 0x11 ;
  uint8_t sync8 = 0x22 ;

} __attribute__((packed));

static_assert(sizeof(serialPacket) == 512, "SerialPacket size must be exactly 512 bytes");

static_assert(offsetof(serialPacket, data) % alignof(uint16_t) == 0, 
              "data array must be properly aligned for uint16_t access");

serialPacket txPacket;

void transmit() {
  txPacket.count += 1;
  #if CAPTURETIMINGS 
    txPacket.timeStamp = micros();
  #endif
  Serial.write((uint8_t*)&txPacket, sizeof(serialPacket));
}

// Function to pulse both CS at once - slightly faster sometimes
void pulseBothCS() {
  digitalWriteFast(CSa, LOW)    ;
  digitalWriteFast(CSb, LOW)    ;
  delayNanoseconds(t_quiet)     ;
  digitalWriteFast(CSa, HIGH)   ;
  digitalWriteFast(CSb, HIGH)   ;
}

// Declaring 'adc's
ADC adcA(CSa, A0a, A1a, A2a, A3a, &SPI);
ADC adcB(CSb, A0b, A1b, A2b, A3b, &SPI1);

// Setup Function
void setup() {
  
  // Initialize Serial monitor for debugging
  Serial.begin(115200);
  // This baude rate is for compatibility
  // It does not do anything and is ignored when compiled for Teensy

  // Initialize SPI
  SPI.begin();
  SPI.beginTransaction(SPISettings(spiClock, MSBFIRST, SPI_MODE2));

  SPI1.setMISO(MISO1);
  SPI1.setMOSI(MOSI1);
  SPI1.setSCK(SCK1);
  SPI1.begin();
  SPI1.beginTransaction(SPISettings(spiClock, MSBFIRST, SPI_MODE2));

  // Wait for powerup
  delayMicroseconds(t_powerup) ;

  // Hard Resets
  adcA.hardReset();
  adcB.hardReset();

  #if SERIALDIAGNOSTICS
  // Wait for serial connection to be established
  while (!Serial)           ;

  Serial.print("wait1 = ")  ;
  Serial.println(wait1)     ;
  #endif

  // ADC CONFIG
  adcA.configADC();
  adcB.configADC();

  delayMicroseconds(cycleWait);
}
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
